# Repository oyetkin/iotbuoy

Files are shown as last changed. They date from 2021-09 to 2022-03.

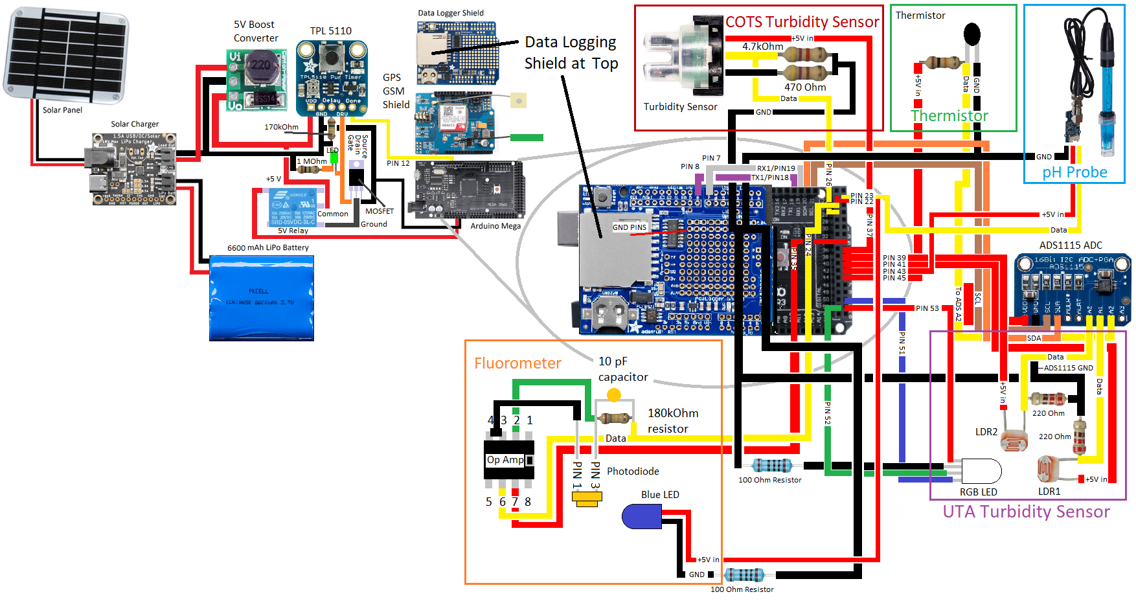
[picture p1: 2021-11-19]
ElectricalSchematic.png

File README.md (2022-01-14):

# IoT Buoy



Lake Erie Algae Bloom 2019, (Image credit NOAA)

An open source, low-cost envirnmental buoy designed to monitor the health of lakes, rivers, estuaries and tidal regions with particular emphasis on algae blooms.
Designed by [Analytical Mechanics Associates](https://www.ama-inc.com/) and the [Virginia Modeling, Analysis & Simulation Center (VMASC)](https://www.odu.edu/vmasc). This project is compatible with the [Open Data Cube](https://www.opendatacube.org/), which is an open-source platform that can ingest data from a variety of sensors and has the goal of making environmental monitoring simple and highly accessible. An overview of the current progress is posted [here](https://github.com/oyetkin/iotbuoy/blob/main/BuoyPresentation1.pdf)

# Building your Buoy - Buoy Specific Hardware Required

### 1. [Arduino MEGA or ELEGOO MEGA](https://www.amazon.com/ELEGOO-ATmega2560-ATMEGA16U2-Arduino-Compliant/dp/B01H4ZDYCE/ref=asc_df_B01H4ZDYCE/?tag=hyprod-20&linkCode=df0&hvadid=309751315916&hvpos=&hvnetw=g&hvrand=11900577637582741809&hvpone=&hvptwo=&hvqmt=&hvdev=c&hvdvcmdl=&hvlocint=&hvlocphy=9008124&hvtargid=pla-493625544636&psc=1&tag=&ref=&adgrpid=67183599252&hvpone=&hvptwo=&hvadid=309751315916&hvpos=&hvnetw=g&hvrand=11900577637582741809&hvqmt=&hvdev=c&hvdvcmdl=&hvlocint=&hvlocphy=9008124&hvtargid=pla-493625544636)

- [Arduino MEGA R3](https://store.arduino.cc/usa/mega-2560-r3)

- [ELEGOO MEGA R3 (cheaper)](https://www.amazon.com/ELEGOO-ATmega2560-ATMEGA16U2-Arduino-Compliant/dp/B01H4ZDYCE/ref=asc_df_B01H4ZDYCE/?tag=hyprod-20&linkCode=df0&hvadid=309751315916&hvpos=&hvnetw=g&hvrand=11900577637582741809&hvpone=&hvptwo=&hvqmt=&hvdev=c&hvdvcmdl=&hvlocint=&hvlocphy=9008124&hvtargid=pla-493625544636&psc=1&tag=&ref=&adgrpid=67183599252&hvpone=&hvptwo=&hvadid=309751315916&hvpos=&hvnetw=g&hvrand=11900577637582741809&hvqmt=&hvdev=c&hvdvcmdl=&hvlocint=&hvlocphy=9008124&hvtargid=pla-493625544636)

### 2. [Adafruit Boost Converter](https://www.amazon.com/Module-Output-Voltage-Converter-Regulator/dp/B08NCM9ZPQ/ref=pd_lpo_2?pd_rd_i=B08NCM9ZPQ&th=1)

### 3. [SIM 808 GPRS/GSM Shield](https://www.robotshop.com/en/sim808-gps-gprsgsm-arduino-shield-mkf.html)

### 4. [Adafruit Solar Charger](https://www.adafruit.com/product/390?gclid=Cj0KCQiAkZKNBhDiARIsAPsk0Wjwwub03ZPgBxlKg1lHWn5nn0opyzVy_Q3VPSugYz3q11KsZ251EOcaAhBzEALw_wcB)

### 5. [Adafruit Data Logging Shield](https://www.adafruit.com/product/1141?gclid=EAIaIQobChMI9OqQ1tr58QIVzXxvBB3GTgbGEAQYASABEgITQvD_BwE)

- Requires [CR1220 Coin Cell Battery](https://www.grainger.com/product/54ZU79?ef_id=CjwKCAjwmeiIBhA6EiwA-uaeFeCfQyJyafe8bUuabPpTv9V-Dkiohqq99VO3asoSj661ExP630XgBhoCccUQAvD_BwE:G:s&s_kwcid=AL!2966!3!496359975085!!!g!484329633033!&gucid=N:N:PS:Paid:GGL:CSM-2293:99F1R6:20501231&gclid=CjwKCAjwmeiIBhA6EiwA-uaeFeCfQyJyafe8bUuabPpTv9V-Dkiohqq99VO3asoSj661ExP630XgBhoCccUQAvD_BwE&gclsrc=aw.ds)

- [Adafruit Data Logging Shield Board and Schematic](https://github.com/adafruit/Data-Logger-shield)

- [Adafruit Data Logging Shield Fritzing Object](https://github.com/adafruit/Fritzing-Library/blob/master/parts/Adafruit%20Datalogger%20Shield%20v1.fzpz)

### 6. [Adafruit ADS1115 Analog to Digital Converter](https://www.adafruit.com/product/1085?gclid=Cj0KCQjw0emHBhC1ARIsAL1QGNfJ3SJ85uZqejbk4At3gi_rBteSZwTxbq5_mKbJvcHG9wJhS_kqJ54aAu4vEALw_wcB)

- [ADS1115 Hardware Drivers](https://github.com/adafruit/Adafruit_ADS1X15)

- [ADS1115 Board and Schematics](https://github.com/adafruit/ADS1X15-Breakout-Board-PCBs)

- [ADS1115 Fritzing Object](https://github.com/adafruit/Fritzing-Library/blob/master/parts/Adafruit%20ADS1115%2016Bit%20I2C%20ADC.fzpz)

- [ADS1115 Data Sheet](https://cdn-shop.adafruit.com/datasheets/ads1115.pdf)

- [ADS1115 Sample Code](https://learn.adafruit.com/adafruit-4-channel-adc-breakouts/arduino-code)

### 7. [Adafruit 6V 3.5W Solar Panel](https://www.adafruit.com/product/500)

- [Solar Panel Technical Drawing](https://github.com/VoltaicEngineering/Solar-Panel-Drawings/blob/master/Voltaic%20Systems%203.5W%206V%20113x210mm%20DRAWING%20CURRENT%202017%207%2020.pdf)

### 10. [6600 mAh 3.7V Lithium Ion Battery](https://www.adafruit.com/product/353)

### 11. [Adafruit TPL5110 Breakout Board](https://www.adafruit.com/product/3435)

### 12. [Adafruit Power Boost 1000 Breakout Board](https://www.adafruit.com/product/2465?gclid=CjwKCAiA24SPBhB0EiwAjBgkhrGJI_mgLnF6EL7C2EgxJwRfddbmznOh6DxHYULQIVquQbLt4znxhRoCKecQAvD_BwE)

### 12. Housing
- Buoy with CAD files provided [here](https://github.com/oyetkin/iotbuoy/tree/main/CAD_Files)

- Waterproof box

- Your own design

# Fluorometer Design

### 1. [1 x 395 nm LED](https://www.mouser.com/ProductDetail/BIVAR/UV5TZ-390-15?qs=sGAEpiMZZMtaWn5d0uiAD8cVjFdgDZGx%2FUxBqCDWrPM%3D)

### 2. [FDS 100 Photodiode](https://www.thorlabs.us/thorproduct.cfm?partnumber=FDS100)

### 3. [550 nm Cut On Long Pass Filter](https://www.newport.com/p/10CGA-550)

### 4. [Jewler's Resin](https://www.amazon.com/16OZ-Epoxy-Resin-Graduated-Instructions/dp/B0839GN3PF/ref=sr_1_5?keywords=clear%2Bepoxy%2Bresin&qid=1638217693&qsid=146-2373950-0512811&s=arts-crafts&sr=1-5&sres=B08233BV5W%2CB08HN2XCDS%2CB0839GN3PF%2CB098918WFB%2CB084PZG6HK%2CB07S1MLQMJ%2CB084Q87Y8M%2CB07YCVVYFK%2CB099XFL1PK%2CB086L1CDMT%2CB07G5HY79C%2CB07JBKDQZJ%2CB07JB5P76Z%2CB089XZJFG5%2CB097JLGFZF%2CB07QF2XYYX%2CB092HX7SQT%2CB08PF576QC%2CB0823LC5H1%2CB08XQ2S1VQ&th=1)

### 5. [Black ABS Filament (will be useful for turbidity sensor as well)](https://www.amazon.com/HATCHBOX-3D-Filament-Dimensional-Accuracy/dp/B00J0H8EWA/ref=sr_1_3?crid=HBAP4Q1YHOWB&keywords=black%2Babs%2Bfilament%2B1.75%2B1kg&qid=1638217775&qsid=146-2373950-0512811&sprefix=black%2Babs%2Bfila%2Carts-crafts%2C167&sr=8-3&sres=B00J0H8EWA%2CB07XF5KM74%2CB07T2QZSLY%2CB01M6Y2QF1%2CB00MV7T25E%2CB07199449V%2CB00WX4UONO%2CB0919Q91MN%2CB015VGJGPW%2CB00F9MNMAY%2CB018F586ES%2CB08N4MMK6V%2CB089NPTH2W%2CB09H7RKL95%2CB07GFXYVLR%2CB08BR7YCY1&srpt=THERMOPLASTIC_FILAMENT&th=1)

# Turbidity Sensor Design

### 1. [2 x Photoresistors](https://www.amazon.com/gp/product/B01N7V536K/ref=ppx_yo_dt_b_search_asin_image?ie=UTF8&psc=1)

### 2. [1 x RGB LED](https://www.amazon.com/gp/product/B077XGF3YR/ref=ppx_yo_dt_b_search_asin_title?ie=UTF8&th=1)

### 3. [Jewler's Resin](https://www.amazon.com/16OZ-Epoxy-Resin-Graduated-Instructions/dp/B0839GN3PF/ref=sr_1_5?keywords=clear%2Bepoxy%2Bresin&qid=1638217693&qsid=146-2373950-0512811&s=arts-crafts&sr=1-5&sres=B08233BV5W%2CB08HN2XCDS%2CB0839GN3PF%2CB098918WFB%2CB084PZG6HK%2CB07S1MLQMJ%2CB084Q87Y8M%2CB07YCVVYFK%2CB099XFL1PK%2CB086L1CDMT%2CB07G5HY79C%2CB07JBKDQZJ%2CB07JB5P76Z%2CB089XZJFG5%2CB097JLGFZF%2CB07QF2XYYX%2CB092HX7SQT%2CB08PF576QC%2CB0823LC5H1%2CB08XQ2S1VQ&th=1)

### 4. [Black ABS Filament (will be useful for fluorometer as well)](https://www.amazon.com/HATCHBOX-3D-Filament-Dimensional-Accuracy/dp/B00J0H8EWA/ref=sr_1_3?crid=HBAP4Q1YHOWB&keywords=black%2Babs%2Bfilament%2B1.75%2B1kg&qid=1638217775&qsid=146-2373950-0512811&sprefix=black%2Babs%2Bfila%2Carts-crafts%2C167&sr=8-3&sres=B00J0H8EWA%2CB07XF5KM74%2CB07T2QZSLY%2CB01M6Y2QF1%2CB00MV7T25E%2CB07199449V%2CB00WX4UONO%2CB0919Q91MN%2CB015VGJGPW%2CB00F9MNMAY%2CB018F586ES%2CB08N4MMK6V%2CB089NPTH2W%2CB09H7RKL95%2CB07GFXYVLR%2CB08BR7YCY1&srpt=THERMOPLASTIC_FILAMENT&th=1)

# Other Items Required

- SD Card
- Jumper wires
- Header pins
- Solder
- Soldering iron
- Wire strippers
- Heat shrink tubing
- Electrical tape
- DP 100 epoxy
- Rope/anchor OR Rope/mooring OR free-floating

# Other Interesting Sensors

- [BME 680 Temperature, Pressure and Humidity Sensor](https://www.adafruit.com/product/3660)

- [DHT-11 Temperature/Humidity Sensor](https://www.adafruit.com/product/386)

- [DHT-22 Temperature/Humidity Sensor](https://www.adafruit.com/product/385)

- [Waterproof Thermistor](https://www.adafruit.com/product/372)

- [pH Sensor - TEKCOPLUS](https://www.amazon.com/Replacement-Electrode-Connector-Controller-Hydroponics/dp/B09681C36B/ref=sr_1_19?dchild=1&keywords=ph+meter+electrode&qid=1629149917&sr=8-19)
OR
- [pH Sensor - Vernier](https://www.vernier.com/product/ph-sensor/)

- [Turbidity Sensor](https://www.digikey.com/en/products/detail/amphenol-advanced-sensors/TSD-10/4767843?utm_adgroup=Sensors%20%26%20Transducers&utm_source=google&utm_medium=cpc&utm_campaign=Dynamic%20Search_EN_RLSA_Buyers&utm_term=&utm_content=Sensors%20%26%20Transducers&gclid=CjwKCAjwmeiIBhA6EiwA-uaeFRJvJ3rLHPiHJND-PSO5aePXsmi2i962wfCCjfp96LtXLJMJ6MAUsBoClz0QAvD_BwE)

- [MPU 6050 Inertial Measurement Unit (for wave height, direction etc.)](https://www.adafruit.com/product/3886)

# Fabrication

- Read the "Complete Guide to Building Your Very Own Algae Monitoring Buoy"

# Viewing Results

- Download jupyter to your computer and run "Visualization_Notebook.ipynb"

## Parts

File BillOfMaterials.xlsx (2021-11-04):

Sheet: Grey ABS Case
COMPONENT | NAME | UNIT PRICE | QUANTITY | TOTAL PRICE | LINK
Solar Panel | Adafruit 1W Solar Panel | $19.95 | 1 | $19.95 | https://www.adafruit.com/product/3809
Microcontroller | ELEGOO Mega | $15.99 | 2 | $31.98 | https://www.amazon.com/ELEGOO-ATmega2560-ATMEGA16U2-Arduino-Compliant/dp/B01H4ZDYCE?hvadid=309751315916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
LoRa Shield | Dragino Shield | $21.00 | 2 | $42.00 | LoRa Long Range Transceiver Shield 915 MHz (North America) - RobotShop (https://www.robotshop.com/en/lora-long-range-transceiver-shield-915-mhz-north-america.html)
Container | 220×170×110mm (8.6"×6.7"×4.3") Gratury Junction Box, Hinged Cover Stainless Steel Latch IP67 Waterproof Plastic Enclosure for Electrical Project Includes Mounting Plate and Wall Bracket | $12.99 | 1 | $12.99 | https://www.amazon.com/Gratury-Stainless-Waterproof-Electrical-290%C3%97190%C3%97140mm/dp/B08281V2RL?ac_md=3-0-VW5kZXIgJDUw-ac_d_pm_pm_pm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
NTC Thermistor | 10k resistor | $0.55 | 2 | $1.10 | https://www.digikey.com/en/products/detail/murata-electronics/NXFT15XH103FA1B025/5797781
Battery | 3.7 V 2.2 Ah battery | $9.95 | 1 | $9.95 | Lithium Ion Cylindrical Battery - 3.7v 2200mAh : ID 1781 : $9.95 : Adafruit Industries, Unique & fun DIY electronics and kits (https://www.adafruit.com/product/1781)
Battery Management System | Solar Lithium Ion/Polymer charger | $9.95 | 1 | $9.95 | https://www.adafruit.com/product/4755
Data logging shield | MicroSD card breakout board+ | $13.95 | 1 | $13.95 | https://www.adafruit.com/product/1141?gclid=EAIaIQobChMI9OqQ1tr58QIVzXxvBB3GTgbGEAQYASABEgITQvD_BwE
IMU | MPU 6050 | $6.95 | 1 | $6.95 | https://www.adafruit.com/product/3886
Boost Converter | Adafruit 5V Boost Converter | $3.56 | 1 | $3.56 | https://www.adafruit.com/product/4654?gclid=EAIaIQobChMI0a7O6eH38QIVCWxvBB0nXAA6EAQYASABEgIBAvD_BwE
GPRS/GSM/GPS Shield | SIM808 | $39.00 | 1 | $39.00 | https://www.robotshop.com/en/sim808-gps-gprsgsm-arduino-shield.html
LTE SIM7600 Breakout |  | $40.00 | 1 | $40.00 | https://it.aliexpress.com/item/4000224044192.html?spm=a2g0o.detail.1000023.5.168266beAIrhDP
ADC | ADS1115 | $14.95 | 1 | $14.95 | https://www.adafruit.com/product/1085
Wide Angle LED |  | $0.21 | 1 | $0.21 | https://lighthouseleds.com/5mm-diffused-flat-top-led-amber-orange-ultra-bright.html
150 ohm resistor |  | $0.73 | 1 | $0.73 | https://www.mouser.com/ProductDetail/TE-Connectivity-Holsworthy/ROX5SSJ150R?qs=sGAEpiMZZMtlubZbdhIBIMLPczR3K4Ue5uevzLwiHc4%3D
Marine Grade Nylon Rope |  | $24.00 | 1 | $24.00 | 3/16" Polyester Rope - White - QualityNylonRope.com (https://www.qualitynylonrope.com/3-16-polyester-rope/)
Hologram Industrial SIM |  | $6.00 | 1 | $6.00 | https://store.hologram.io/store/global-iot-sim-card/51
DP 100 Epoxy |  | $26.16 | 1 | $26.16 | SCOTCH-WELD Series DP100, Epoxy Adhesive, Dual-Cartridge, 1.64 oz, Clear, Not Specified Work Life - 489J86|100 - Grainger (https://www.grainger.com/product/SCOTCH-WELD-Series-DP100-489J86?req=Customer_Also_Viewed&opr=AZIDPRR_RRAD-051820&analytics=recommendation)
CR1220 Coin Battery for RTC |  | $0.72 | 1 | $0.72 | GRAINGER APPROVED 1220, Button Cell Battery, Lithium, 3V DC, Diameter 0.472 in, Depth 0.078 in - 54ZU79|CR1220 - Grainger (https://www.grainger.com/product/54ZU79?gucid=N:N:PS:Paid:MS:CSM-2293:MOO74J:20501231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)
SD Card |  | $12.49 | 1 | $12.49 | https://www.amazon.com/SanDisk-Extreme-32GB-UHS-I-SDSDXXG-032G-GN4IN/dp/B01J5RHBQ4?ac_md=3-2-MzIgR0I%3D-ac_d_mf_rf_rf&cv_ct_cx=sd+card
Zip Ties |  | $4.99 | 1 | $4.99 | Amazon.com: TR Industrial Multi-Purpose UV Resistant Black Cable Ties, 4 inches, 100 Pack : Electronics (https://www.amazon.com/TR-Industrial-TR88301-Multi-Purpose-Cable/dp/B01018DB2E?s=hi)
JST Connectors |  | $7.99 | 1 | $7.99 | Amazon.com: 10pcs Upgraded Tiny Whoop JST-PH 2.0 Male and Female Connector Cable for Battery JJRC H36 H67 Blade Inductrix E010 E013 : Toys & Games (https://www.amazon.com/Upgraded-Connector-Battery-Inductrix-Eachine/dp/B07NWD5NTN?hvadid=80195684681837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)
Heat shrink tubing |  | $6.49 | 1 | $6.49 | https://www.amazon.com/560PCS-Heat-Shrink-Tubing-Eventronic/dp/B072PCQ2LW?hvadid=198097502341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
5.5 mm Barrel Connectors |  | $1.70 | 2 | $3.40 | FIT0043 DFRobot | Battery Products | DigiKey (https://www.digikey.com/en/products/detail/dfrobot/FIT0043/7597082)
Jumper wires |  | $5.99 | 1 | $5.99 | Amazon.com: EDGELEC 120pcs Breadboard Jumper Wires 10cm 15cm 20cm 30cm 40cm 50cm 100cm Wire Length Optional Dupont Cable Assorted Kit Male to Female Male to Male Female to Female Multicolored Ribbon Cables : Electronics (https://www.amazon.com/EDGELEC-Breadboard-Optional-Assorted-Multicolored/dp/B07GD2BWPY)
Solder |  | $8.99 | 1 | $8.99 | YI LIN 60/40 Solder Tin Lead Rosin Core Solder Wire For Electrical Soldering (0.6mm/100g) - - Amazon.com (https://www.amazon.com/YI-LIN-Electrical-Soldering-0-22lbs/dp/B08RHMPJW3?s=industrial)
 |  |  | Sum | $354.49

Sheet: 3D Printed Buoy
COMPONENT | NAME | UNIT PRICE | QUANTITY | TOTAL PRICE | LINK
Solar Panel | Adafruit 1W Solar Panel | $19.95 | 1 | $19.95 | https://www.adafruit.com/product/3809
Microcontroller | ELEGOO Mega | $15.99 | 2 | $31.98 | https://www.amazon.com/ELEGOO-ATmega2560-ATMEGA16U2-Arduino-Compliant/dp/B01H4ZDYCE?hvadid=309751315916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
White ABS Filament |  | $21.99 | 1 | $21.99 | https://www.hatchbox3d.com/collections/abs-1-75mm/products/3d-abs-1kg1-75-wht
Battery | 3.7 V 6.6 Ah battery | $24.50 | 1 | $24.50 | https://www.adafruit.com/product/353
Battery Management System | Solar Lithium Ion/Polymer charger | $9.95 | 1 | $9.95 | https://www.adafruit.com/product/4755
Data logging shield | MicroSD card breakout board+ | $13.95 | 1 | $13.95 | https://www.adafruit.com/product/1141?gclid=EAIaIQobChMI9OqQ1tr58QIVzXxvBB3GTgbGEAQYASABEgITQvD_BwE
Boost Converter | Adafruit 5V Boost Converter | $3.56 | 1 | $3.56 | https://www.adafruit.com/product/4654?gclid=EAIaIQobChMI0a7O6eH38QIVCWxvBB0nXAA6EAQYASABEgIBAvD_BwE
GPRS/GSM/GPS Shield | SIM808 | $39.00 | 1 | $39.00 | https://www.robotshop.com/en/sim808-gps-gprsgsm-arduino-shield.html
ADC | ADS1115 | $14.95 | 1 | $14.95 | https://www.adafruit.com/product/1085
Silicone Sealant |  | $4.25 | 1 | $4.25 | Amazon.com: Henkel Corporation 908570 2.7 oz Tub Clear Silicone Waterproof Sealant, Single Tube, 2 Fl Oz : Industrial & Scientific (https://www.amazon.com/Loctite-Silicone-Waterproof-2-7-Ounce-908570/dp/B0002BBX3U)
Wide Angle LED |  | $0.21 | 1 | $0.21 | https://lighthouseleds.com/5mm-diffused-flat-top-led-amber-orange-ultra-bright.html
150 ohm resistor |  | $0.73 | 1 | $0.73 | https://www.mouser.com/ProductDetail/TE-Connectivity-Holsworthy/ROX5SSJ150R?qs=sGAEpiMZZMtlubZbdhIBIMLPczR3K4Ue5uevzLwiHc4%3D
Marine Grade Nylon Rope |  | $24.00 | 1 | $24.00 | 3/16" Polyester Rope - White - QualityNylonRope.com (https://www.qualitynylonrope.com/3-16-polyester-rope/)
Folding Grapnel Anchor (If no moorings available) |  | $9.99 | 1 | $9.99 | SUNCOR Folding Grapnel Anchors | West Marine (https://www.westmarine.com/buy/suncor--1-1-2-lb-folding-grapnel-anchor--P005_153_003_004?pCode=598813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)
CR1220 Coin Battery for RTC |  | $0.72 | 1 | $0.72 | GRAINGER APPROVED 1220, Button Cell Battery, Lithium, 3V DC, Diameter 0.472 in, Depth 0.078 in - 54ZU79|CR1220 - Grainger (https://www.grainger.com/product/54ZU79?gucid=N:N:PS:Paid:MS:CSM-2293:MOO74J:20501231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)
SD Card |  | $12.49 | 1 | $12.49 | https://www.amazon.com/SanDisk-Extreme-32GB-UHS-I-SDSDXXG-032G-GN4IN/dp/B01J5RHBQ4?ac_md=3-2-MzIgR0I%3D-ac_d_mf_rf_rf&cv_ct_cx=sd+card
Things Mobile SIM Card with $10 euros ($11.56 pre-loaded) |  | $11.56 | 1 | $11.56 | https://www.thingsmobile.com/business/shop
DP 100 Epoxy |  | $26.16 | 1 | $26.16 | SCOTCH-WELD Series DP100, Epoxy Adhesive, Dual-Cartridge, 1.64 oz, Clear, Not Specified Work Life - 489J86|100 - Grainger (https://www.grainger.com/product/SCOTCH-WELD-Series-DP100-489J86?req=Customer_Also_Viewed&opr=AZIDPRR_RRAD-051820&analytics=recommendation)
JST Connectors |  | $7.99 | 1 | $7.99 | Amazon.com: 10pcs Upgraded Tiny Whoop JST-PH 2.0 Male and Female Connector Cable for Battery JJRC H36 H67 Blade Inductrix E010 E013 : Toys & Games (https://www.amazon.com/Upgraded-Connector-Battery-Inductrix-Eachine/dp/B07NWD5NTN?hvadid=80195684681837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)
5.5 mm Barrel Connectors |  | $8.49 | 1 | $8.49 | Amazon.com: VONVOFF DC Power Pigtail Cable,18AWG Male and Female DC Connector Plug,12V 5A Barrel Jack Connector for CCTV Security Camera and Lighting Power Adapter (10 Pairs) : Electronics (https://www.amazon.com/VONVOFF-Pigtail-Connector-Security-Lighting/dp/B086DKWJ2H?pd_)
Heat shrink tubing |  | $6.49 | 1 | $6.49 | https://www.amazon.com/560PCS-Heat-Shrink-Tubing-Eventronic/dp/B072PCQ2LW?hvadid=198097502341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
Jumper wires |  | $5.99 | 1 | $5.99 | Amazon.com: EDGELEC 120pcs Breadboard Jumper Wires 10cm 15cm 20cm 30cm 40cm 50cm 100cm Wire Length Optional Dupont Cable Assorted Kit Male to Female Male to Male Female to Female Multicolored Ribbon Cables : Electronics (https://www.amazon.com/EDGELEC-Breadboard-Optional-Assorted-Multicolored/dp/B07GD2BWPY)
Solder |  | $8.99 | 1 | $8.99 | YI LIN 60/40 Solder Tin Lead Rosin Core Solder Wire For Electrical Soldering (0.6mm/100g) - - Amazon.com (https://www.amazon.com/YI-LIN-Electrical-Soldering-0-22lbs/dp/B08RHMPJW3?s=industrial)
Real Time Clock |  | $5.99 | 1 | $5.99 | https://www.diymore.cc/products/diymore-ds3231-at24c32-iic-precision-real-time-clock-memory-module-for-arduino
Relay |  | $3.35 | 1 | $3.35 | https://www.digikey.com/en/products/detail/nte-electronics | -inc/R73-1D10-5%2F6/11655844?utm_adgroup=General&utm_source=google&utm_medium=cpc&utm_campaign=Shopping_DK%2BSupplier_NTE%20Electronics&utm_term=&utm_content=General&gclid=CjwKCAjwiY6MBhBqEiwARFSCPvk5GTMvMUVIlpouOziBqMiKNzt5CrrNAmKSv3wozyIH78KfpWLppRoCd9YQAvD_BwE
IRL 7833 MOSFET (needed in fluorometer also) |  | $1.91 | 1 | $1.91 | https://www.mouser.com/ProductDetail/Infineon-IR/IRL7833PBF?qs=9%252BKlkBgLFf3m53w7MGFaEw%3D%3D
 |  |  | Total | $319.14

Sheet: Buoy Sensors
COMPONENT | NAME | UNIT PRICE | QUANTITY | TOTAL PRICE | LINK
pH PROBE
pH Meter |  | $29.50 | 1 | $29.50 | https://www.dfrobot.com/product-1025.html
COMMERCIAL TURBIDITY SENSOR
Turbidity Sensor | TSD-10 | $9.04 | 1 | $9.04 | TSD-10 Amphenol Thermometrics | Sensors, Transducers | DigiKey (https://www.digikey.com/en/products/detail/amphenol-advanced-sensors/TSD-10/4767843)
BME 280 PRESSURE, TEMPERATURE, HUMIDITY SENSOR
BME 280 |  | $14.99 | 1 | $14.99 | https://www.amazon.com/HiLetgo-Atmospheric-Pressure-Temperature-Humidity/dp/B01N47LZ4P
CUSTOM TURBIDITY SENSOR
RGB LED | HV-5RGB25 | $1.05 | 2 | $2.10 | https://www.digikey.com/en/products/detail/inolux-corporation/HV-5RGB25/7604615
Photoresistor | Adafruit photoresistor | $0.95 | 2 | $1.90 | https://www.digikey.com/en/products/detail/adafruit-industries-llc/161/7244927
1 x 100 Ohm Resistor
2 x 220 Ohm Resistors
Magnets
Pipe Cleaners
INERTIAL MEASUREMENT UNIT
IMU | MPU 6050 | $6.95 | 1 | $6.95 | https://www.adafruit.com/product/3886
WATER TEMPERATURE SENSOR
Epoxy Waterproof 10k Thermistor |  | $4.00 | 1 | $4.00 | https://www.adafruit.com/product/372
10 kOhm Resistor
FLUOROMETER
Red Filter | Newport 610 nm filter | $48.00 | 1 | $48.00 | 10CGA-550 Longpass Filter (newport.com) (https://www.newport.com/p/10CGA-550) | https://www.1stoplighting.com/lighting/11-224-10327-0-660832/Nora-Lighting_Lens-for-MR16-NM-100R-MR16.htm?nsoid=2639140&CAWELAID=230004010008913043
Operational Amplifier | OP07 | $2.92 | 1 | $2.92 | https://www.mouser.com/ProductDetail/Analog-Devices/OP07CPZ?qs=WIvQP4zGaninz564Y%252B7wyA%3D%3D
Photodiode | FDS100 | $14.94 | 1 | $14.94 | https://www.thorlabs.us/thorproduct.cfm?partnumber=FDS100
Capacitor | 1 nF | $0.71 | 1 | $0.71 | https://www.mouser.com/ProductDetail/Vishay-Cera-Mite/561R10TCCQ10?qs=ohMLqj34oV1qAxjp44jWYQ%3D%3D
Optically Clear Resin |  | $11.99 | 1 | $11.99 | Amazon.com: Clear Epoxy Resin Art Resin Kit 16 Ounce Crystal Jewelry Resin 2 Part Epoxy Resin Kit with Bonus Measuring Cups Sticks Spreader and Gloves : Arts, Crafts & Sewing
Lens |  | $35.00 | 1 | $35.00 | Thorlabs - LA1540-AB N-BK7 Plano-Convex Lens, Ø1/2", f = 15 mm, AR Coating: 400 - 1100 nm (https://www.thorlabs.com/thorproduct.cfm?partnumber=LA1540-AB)
UV LED |  | $1.99 | 2 | $3.98 | UV5TZ-390-15 Bivar | Mouser (https://www.mouser.com/ProductDetail/Bivar/UV5TZ-390-15?qs=cy%252BcHHACsGLfBNaawfbUXg%3D%3D)
IRL7833 MOSFET |  | $1.91 | 1 | $1.91 | https://www.mouser.com/ProductDetail/Infineon-IR/IRL7833PBF?qs=9%252BKlkBgLFf3m53w7MGFaEw%3D%3D
80 x 20 mm Perf Board |  |  |  | $0.00
220 kOhm Resistor |  |  |  | $0.00
6 x 5.6 Mohm Resistors |  |  |  | $0.00
1 x 0.1 Ohm Resistor |  |  |  | $0.00
Electrical Tape |  |  |  | $0.00
Small vial (roughly 1/2 - 3/4 inch diameter should be fine) |  | $4.79 | 1 | $4.79 | https://www.amazon.com/Glass-Vials-Dram-Pack-12/dp/B002JV89OC
Silicone Grease |  | $4.28 | 1 | $4.28 | https://www.amazon.com/gp/product/B000DZFUPC/ref=ppx_yo_dt_b_search_asin_title?ie=UTF8&psc=1
Felt Pieces |  |  |  | $0.00
Set Screws |  |  |  | $0.00
316 Stainless Steel Shaft |  | $5.19 | 1 | $5.19 | https://www.mcmaster.com/1263K133/
O rings |  | $2.32 | 4 | $9.28 | https://www.mcmaster.com/5308T115/
9 g servo (see column G if not available) |  | $6.99 | 1 | $6.99 | Amazon.com: MMOBIEL SG90 9g Micro Servo Motor Kit for RC Drone/Car/Airplane/Helicopter/Vehicles/Robots/Compatible with Arduino Projects and Raspberry Pi Incl. Screws and 3 Servo Arms : Toys & Games (https://www.amazon.com/MMOBIEL-Airplane-Helicopter-Compatible-Raspberry/dp/B097RD8RB7?s=industrial) | Amazon.com: 4Pcs SG90 9g Micro Servos for RC Robot Helicopter Airplane Controls Car Boat : Toys & Games (https://www.amazon.com/Micro-Servos-Helicopter-Airplane-Controls/dp/B07MLR1498?s=industrial)
 |  |  | Total | $218.46

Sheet: Old PCB
COMPONENT NAME | UNIT PRICE | QUANTITY | TOTAL PRICE | SPECS | LINK
Female Headers, I2C | $0.45 | 2 | $0.90 | 1x4, 2.54mm spacing | https://www.digikey.com/en/products/detail/sullins-connector-solutions/PPTC041LFBN-RC/810144
Female Headers, ESP | $0.98 | 2 | $1.96 | 1x15, 2.54mm spacing | https://www.digikey.com/en/products/detail/sullins-connector-solutions/PPTC151LFBN-RC/810153
Female Header, IR Receiver | $0.42 | 1 | $0.42 | 1x3, 2.54mm spacing | https://www.digikey.com/en/products/detail/sullins-connector-solutions/PPTC031LFBN-RC/810143
Transistor, logic inverting and 38KHz modulation | $0.67 | 2 | $1.34 | SOT-23 package | https://www.digikey.com/en/products/detail/diodes-incorporated/ZXTN07045EFFTA/1557734
Resistors, button and other pullup | $0.10 | 3 | $0.30 | 10K Ohm, 0805 package | https://www.digikey.com/en/products/detail/bourns-inc/CR0805-FX-1002ELF/3593209
Resistors, I2C Pullup | $0.10 | 2 | $0.20 | 2.4K Ohm, 0805 package | https://www.digikey.com/en/products/detail/bourns-inc/CR0805-FX-2401ELF/3784778
Resistors, logic inverter | $0.10 | 1 | $0.10 | 100K Ohm, 0805 package | https://www.digikey.com/en/products/detail/te-connectivity-passive-product/CRG0805F100K/2380829
Resistors, IR LED | $0.10 | 2 | $0.20 | 220 Ohm, 0805 package | https://www.digikey.com/en/products/detail/bourns-inc/CR0805-FX-2200ELF/3784749
Resistors, IR Receiver | $0.10 | 1 | $0.10 | 200 Ohm, 0805 package | https://www.digikey.com/en/products/detail/bourns-inc/CR0805-FX-2000ELF/3784732
Resistors, LED driver | $0.37 | 1 | $0.37 | 100 Ohm, 0805 package | https://www.digikey.com/en/products/detail/koa-speer-electronics-inc/RK73G2ATTD1000D/13576043
Polarized Capacitor, IR Receiver | $0.70 | 1 | $0.70 | Tantalum, 1.25 x 1.05mm pads | https://www.digikey.com/en/products/detail/avx-corporation/F981C105MMA/4005059
Momentary Button (Mode, Trigger) | $0.61 | 2 | $1.22 | 1 Pole 1 throw, 6x6mm | https://www.digikey.com/en/products/detail/apem-inc/MJTP1138BTR/1795451
IR LED | $0.81 | 2 | $1.62 | 950nm IR emitter | https://www.digikey.com/en/products/detail/osram-opto-semiconductors-inc/SFH-4545/2205955
TSOP382X Photodiode | $1.12 | 1 | $1.12 | 950 nm, 38kHz | https://www.digikey.com/en/products/detail/vishay-semiconductor-opto-division/TSOP38238/1681362
ESP32 | $8.99 | 2 | $17.98 |  | https://www.amazon.com/dp/B079PVCF2G?psc=1&ref=ppx_yo2_dt_b_product_details
BME 280 Breakout Board | $14.99 | 1 | $14.99 |  | https://www.amazon.com/HiLetgo-Atmospheric-Pressure-Temperature-Humidity/dp/B01N47LZ4P
 |  | Total | $43.52

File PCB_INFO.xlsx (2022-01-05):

SUBSYSTEM | COMPONENT | PURPOSE | QUANTITY | UNIT COST | TOTAL COST | SYMBOL | FOOTPRINT | LINK
Communications | SIM7600A-H | GPS/GPRS/LTE Chip | 1 | 1 | Waiting on response |  |  | https://www.simcom.com/product/SIM7600G_R2.html
Communications | 3.7V LDO | Regulate voltage to SIM7600A 3.4-4.2V Power Supply | 1 | 0.7 | 0.7 |  |  | https://www.mouser.com/ProductDetail/Texas-Instruments/LP5907UVX37-NOPB?qs=SmtJf7EgX8RlmYCt%2FlRL3A%3D%3D
Communications | MicroFL Connector | GPS/GPRS/LTE Connection | 3 | 1.22 | 3.66 |  |  | https://www.digikey.com/en/products/detail/hirose-electric-co-ltd/U-FL-R-SMT-10/513011
Communications | Micro Simcard holder | Hold Sim Card | 1 | 1.75 | 1.75 |  |  | https://www.digikey.com/en/products/detail/wurth-electronics-inc/693043020611/5047621
Power | IRL7833 | Power Switching | 1 | 1.91 | 1.91 |  |  | IRL7833PBF Infineon / IR | Mouser (https://www.mouser.com/ProductDetail/Infineon/IRL7833PBF)
Power | Diode | Power system | 1 | $0.03 | 0.034 |  |  | https://www.digikey.com/en/products/detail/diodes-incorporated/1N4007-T/76454
Power | 100 kOhm Sliding Potentiometer | Set Delay Period | 2 | $1.50 | 3 |  |  | https://www.digikey.com/en/products/detail/bourns-inc./PTA3043-2015DPA104/6153411
Power | TPL 5110 | Timer/Power MOSFET | 1 | 0.706 | 0.706 |  |  | TPL5110DDCT | Buy TI parts | TI.com (https://www.ti.com/store/ti/en/p/product/?p=TPL5110DDCT)
Power | Solar Panel Barrel Connector | Connect to solar panel | 1 | 0.99 | 0.99 |  |  | https://www.digikey.com/en/products/detail/w%C3%BCrth-elektronik/694108301002/5047524
Power | DC DC Converter | Solar charge management | 1 | 13.06 | 13.06 |  |  | https://www.digikey.com/en/products/detail/analog-devices-inc/LTM4624IY-PBF/4291840
Power | (2 A limit) Relay | Turn on and off board | 1 | 3.96 | 3.96 |  |  | https://www.digikey.com/en/products/detail/omron-electronics-inc-emc-div/G3VM-41AY1/5799756
Power | Switch | On/off switch | 1 | 0.76 | 0.76 |  |  | https://www.digikey.com/en/products/detail/e-switch/EG1218/101726?s=N4IgTCBcDaIKYHMAEBGAnABgMwgLoF8g
Power | 1 Mohm Resistor | TPL 5110 drive pin grounding | 1 | 0.42 | 0.42 |  |  | CHV1206AJW-105ELF Bourns | Mouser (https://www.mouser.com/ProductDetail/Bourns/CHV1206AJW-105ELF?qs=QNEnbhJQKvbtExCLSyT8ig%3D%3D)
Power | MAX17205G | Voltage/current monitor | 1 | 4.19 | 4.19 |  |  | https://www.mouser.com/ProductDetail/Maxim-Integrated/MAX17205G+T?qs=sO%2FZ8XQFeM14gpZbIvukxg%3D%3D
Power | 4.7 V Zener Diode | Prevent current from flowing to done pin unless at least 4.8 volts | 1 | 0.46 | 0.46 |  |  | https://www.digikey.com/en/products/detail/diodes-incorporated/PD3Z284C4V7-7/1629588
Power | 2.2 kOhm Resistor | Allow done pin to be connected to GND | 1 | 0.12 | 0.12 |  |  | https://www.digikey.com/en/products/detail/koa-speer-electronics-inc/RK73H1JRTTD2201F/12314793
Turbidity Sensor | 220 Ohm Resistor | Turbidity Sensor | 2 | 0.2 | 0.4 |  |  | https://www.mouser.com/ProductDetail/ROHM-Semiconductor/KTR18EZPF2200?qs=sGAEpiMZZMvjAcTDbo5QThnsiMdPc2N4pYMPSxNsWmg%3D
Turbidity Sensor | 10 p connector | Connect turbidity sensor | 1 | 1.4 | 1.4 |  |  | https://www.mouser.com/ProductDetail/TE-Connectivity/1658621-1?qs=AplfTeSvkkCrmD6FuTzFgg%3D%3D&mgh=1
Turbidity Sensor | 10 p connector | Connect turbidity sensor | 1 | 1.3 | 1.3 |  |  | https://www.mouser.com/ProductDetail/TE-Connectivity/5103309-1?qs=84A%2FDAdkstL1A8M23HoAPw%3D%3D
Turbidity Sensor | 100 Ohm Resistor | So LED doesn't burn out | 1
Comm Turbidity Sensor | 3 pin JST | Connector | 1 | 0.25 | 0.25 |  |  | https://www.digikey.com/en/products/detail/jst-sales-america-inc./B03B-XASK-1(LF)(SN)/1634731
Comm Turbidity Sensor | 4.7kOhm | Resistor | 1 | 0.7 | 0.7 |  |  | https://www.mouser.com/ProductDetail/Bourns/CHP1206AFX-4701ELF
Comm Turbidity Sensor | 470 Ohm | Resistor | 1 | 0.32 | 0.32 |  |  | https://www.mouser.com/ProductDetail/Vishay/RCC1206470RFKEA
Fluorometer | 1 nF Capacitor | Fluorometer Smoothing | 1 | 0.33 | 0.33 |  |  | NFM21CC102R1H3D Murata Electronics | Mouser (https://www.mouser.com/ProductDetail/Murata/NFM21CC102R1H3D)
Fluorometer | 0.1 Ohm Resistor | Sensor Gain | 1 | 0.51 | 0.51 |  |  | https://www.digikey.com/en/products/detail/ohmite/WHBR10FET/678833
Fluorometer | LM358 Op Amp | Transimpedance Amplifier Signal | 1 | 0.9 | 0.9 |  |  | https://www.mouser.com/ProductDetail/Texas-Instruments/TL031IP?qs=odmYgEirbwxA1%252BIWuhLCrQ%3D%3D&mgh=1
Fluorometer | IRL7833 | Power Switching | 1 | 1.91 | 1.91 |  |  | IRL7833PBF Infineon / IR | Mouser (https://www.mouser.com/ProductDetail/Infineon/IRL7833PBF)
Fluorometer | 100 Ohm Resistor | So LED doesn't burn out | 1 | 0.32 | 0.32 |  |  | https://www.mouser.com/ProductDetail/Vishay/RCC1206100RFKEA
Fluorometer | 3 pin JST | Connector | 1 | 0.25 | 0.25 |  |  | https://www.digikey.com/en/products/detail/jst-sales-america-inc./B03B-XASK-1(LF)(SN)/1634731
Fluorometer | 36 Mohm Resistor | Sensor Gain | 1 | 0.72 | 0.72 |  |  | CRCW120636M0JPTAHR Vishay / Dale | Mouser (https://www.mouser.com/ProductDetail/Vishay/CRCW120636M0JPTAHR?qs=sGAEpiMZZMsDgH01pahWBgNLWPHBBwkbPRWtvQgSyR0%3D)
Thermistor | 10k Resistor | Voltage Divider |  |  | 0
Thermistor | 3 pin JST | Connector | 1 | 0.25 | 0.25 |  |  | https://www.digikey.com/en/products/detail/jst-sales-america-inc./B03B-XASK-1(LF)(SN)/1634731
Data Management | SD Card Slot | Micro SD card holder | 1 | 2.12 | 2.12 |  |  | 1040310811 Molex | Connectors, Interconnects | DigiKey (https://www.digikey.com/en/products/detail/molex/1040310811/2370379)
Biofouling | 3 pin JST for stepper motor | Connector | 2 | 0.26 | 0.52 |  |  | https://www.mouser.com/ProductDetail/TE-Connectivity/640457-3?qs=sGAEpiMZZMsyYdr3R27aV9Cjae2oalzY
 |  |  |  |  | 50.86
 | Lock in amplifier |  | 1 |  | 0
 | DHT11 |  | 1 |  | 0
 | ADS1115 | Chip Shortage | 1 |  | 0
 | MPU6050 | Chip Shortage | 1 |  | 0
 | INA260 | Chip Shortage | 1 |  | 0
 | Adjustable Gain? | https://www.digikey.com/en/products/detail/amphenol-piher-sensing-systems/PTC15GV02-106A2020-E/14695237

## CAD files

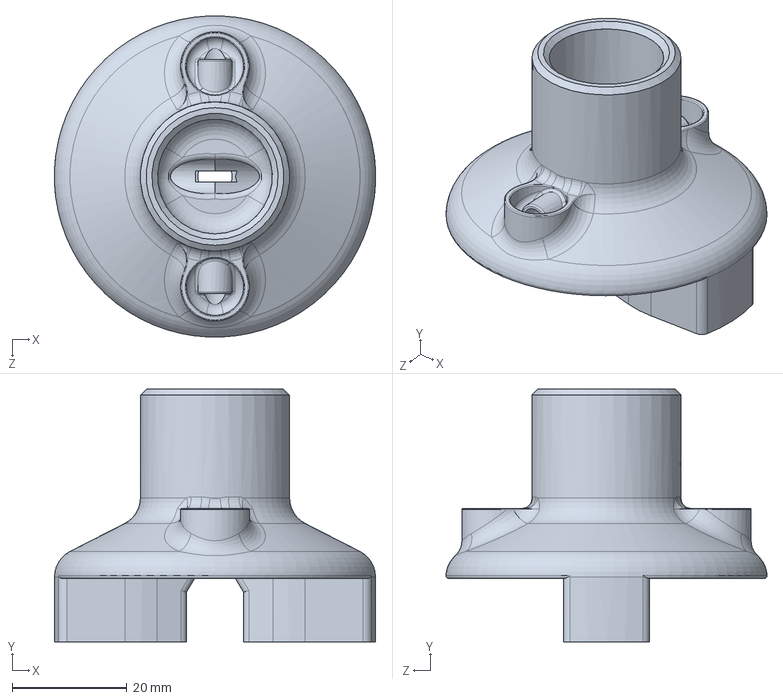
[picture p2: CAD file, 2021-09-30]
CAD_Files/WS 1_Main Body v2.SLDPRT
56.0 x 44.0 x 55.9 mm

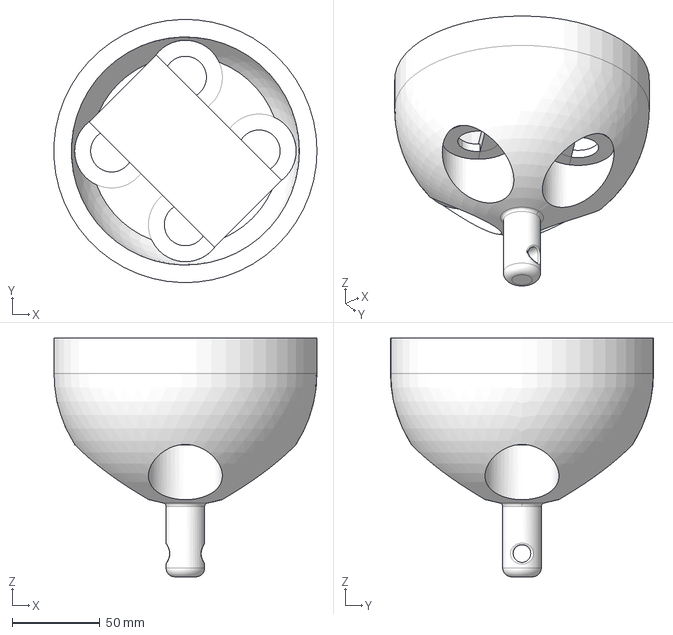
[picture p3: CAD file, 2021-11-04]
CAD_Files/Buoy3DBase.FCStd
149.9 x 149.9 x 136.0 mm

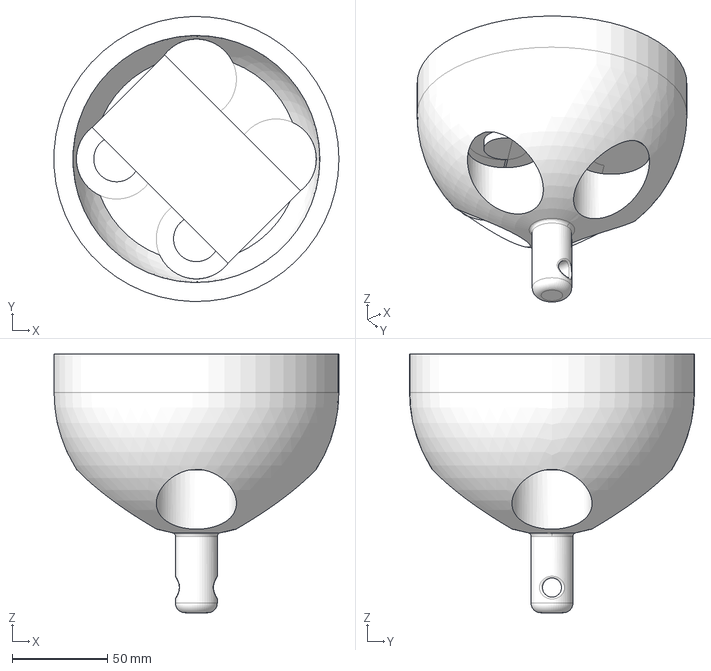
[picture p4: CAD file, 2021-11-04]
CAD_Files/Buoy3DBase-Body.step
149.9 x 149.9 x 136.0 mm

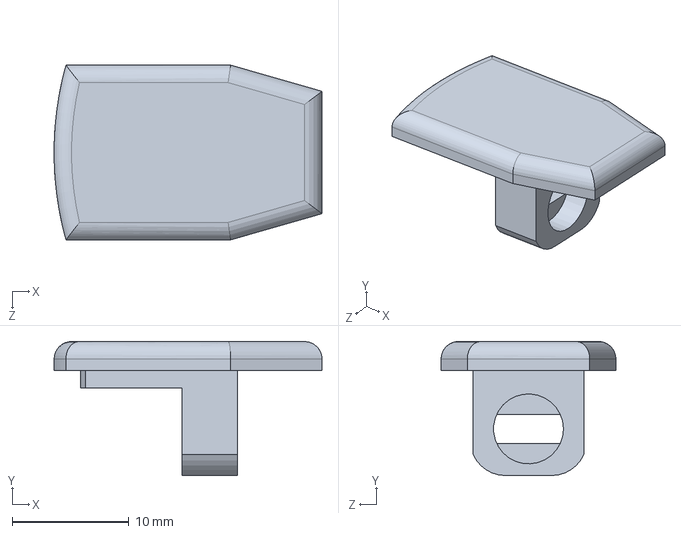
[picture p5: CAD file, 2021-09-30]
CAD_Files/LDR mount v2.SLDPRT
23.0 x 11.5 x 15.0 mm

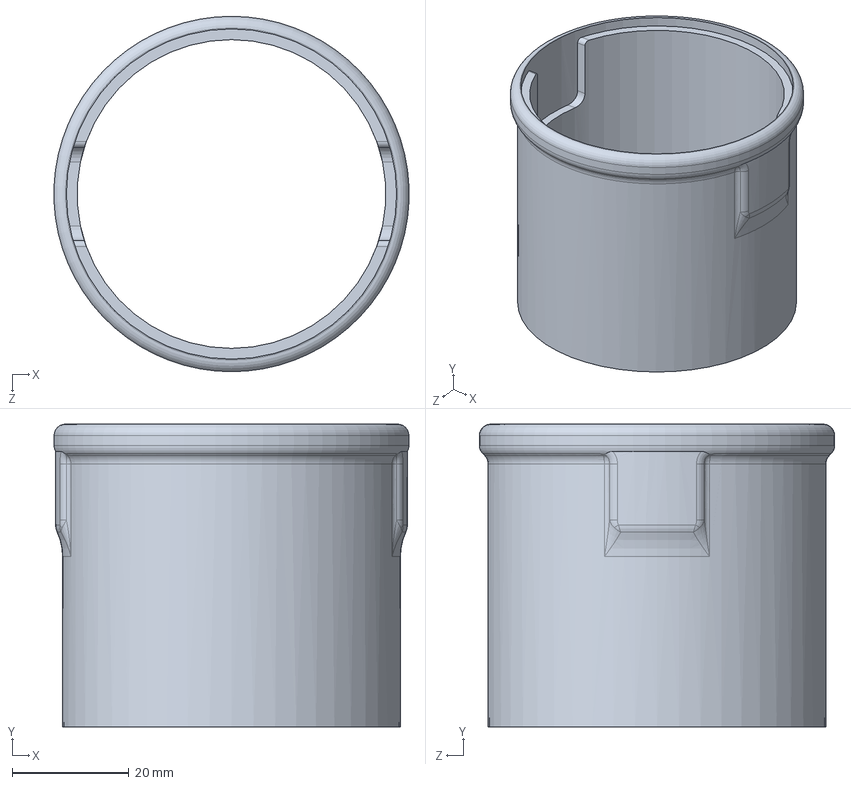
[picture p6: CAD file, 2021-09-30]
CAD_Files/WS 1_Shroud v2.SLDPRT
60.9 x 52.0 x 61.0 mm

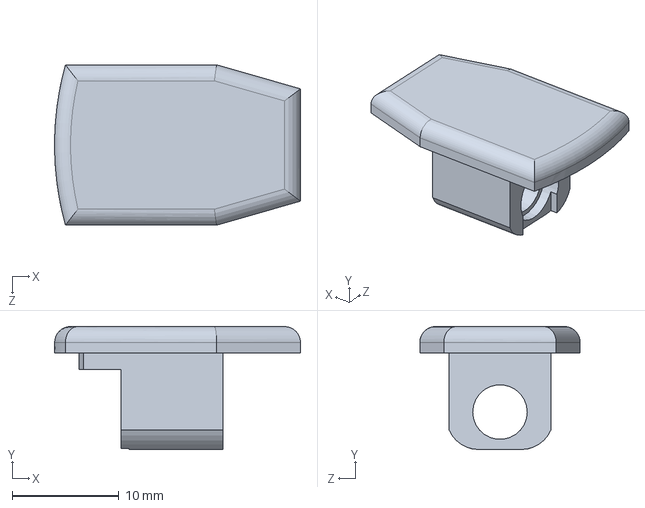
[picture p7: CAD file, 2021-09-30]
CAD_Files/LED mount v2.SLDPRT
23.0 x 11.5 x 15.0 mm

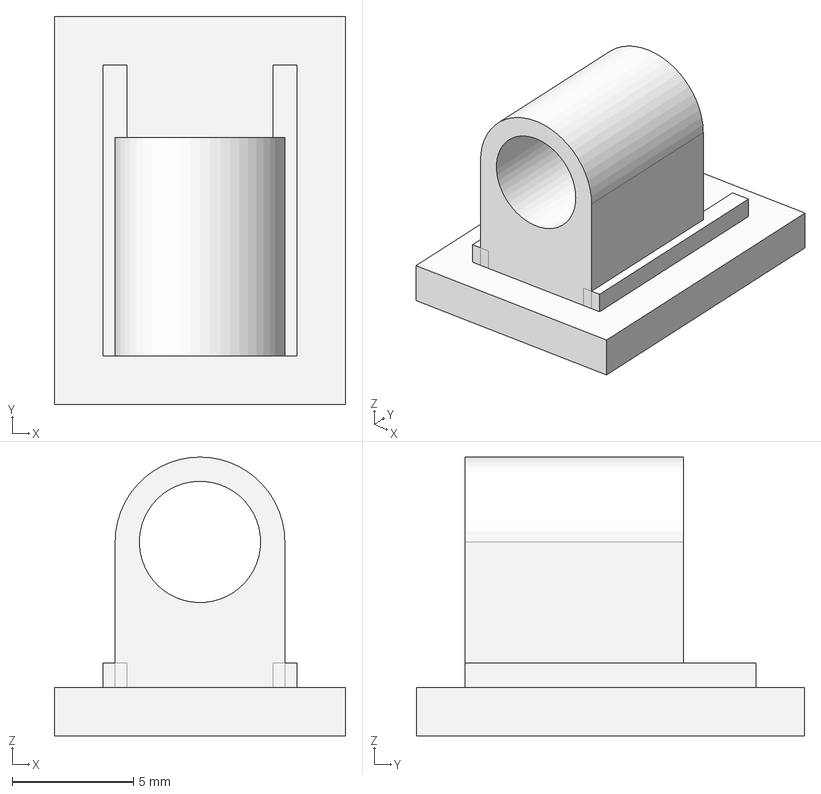
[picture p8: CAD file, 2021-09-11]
CAD_Files/FluorometerLEDHolder.step
12.0 x 16.0 x 11.5 mm

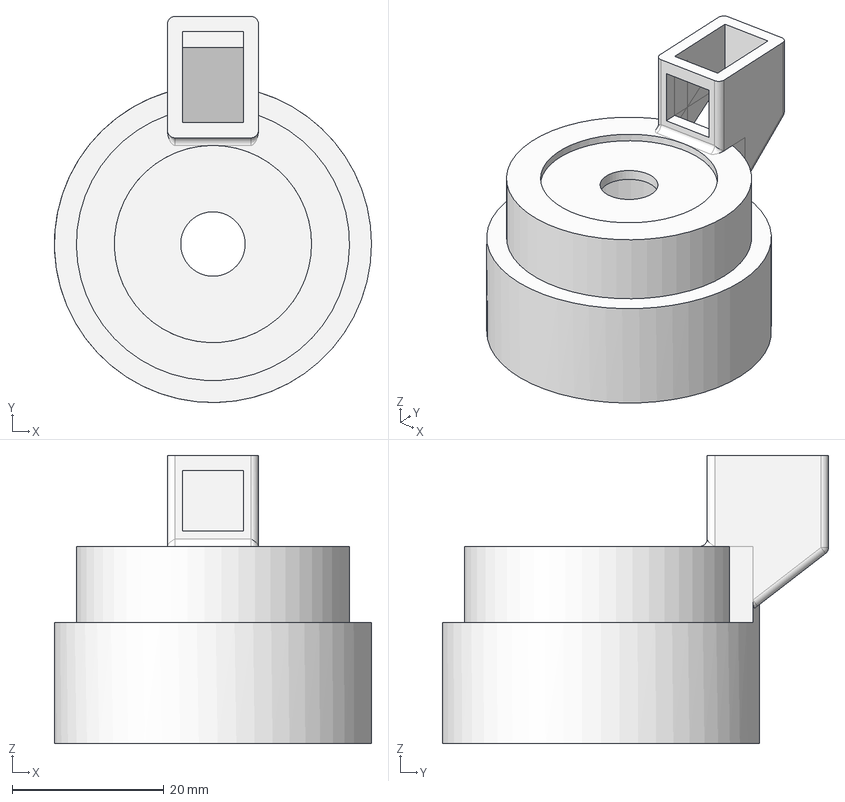
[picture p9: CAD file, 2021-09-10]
CAD_Files/Fluorometer.step
41.8 x 50.9 x 38.0 mm

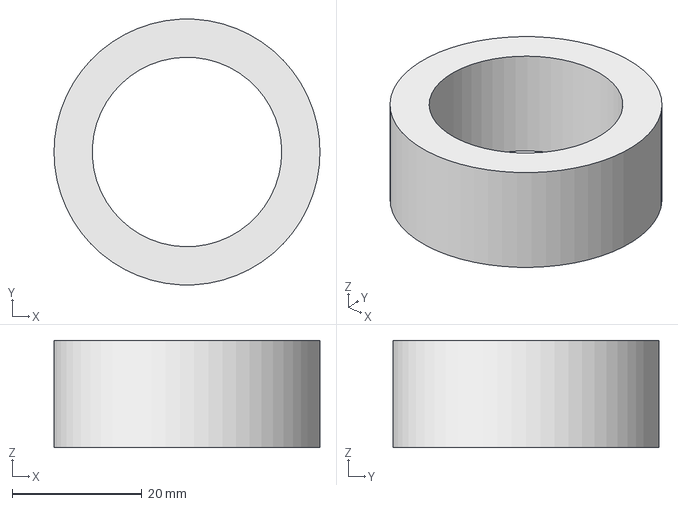
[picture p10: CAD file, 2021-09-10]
CAD_Files/TurbidityAdapter1.FCStd
41.0 x 40.9 x 16.5 mm

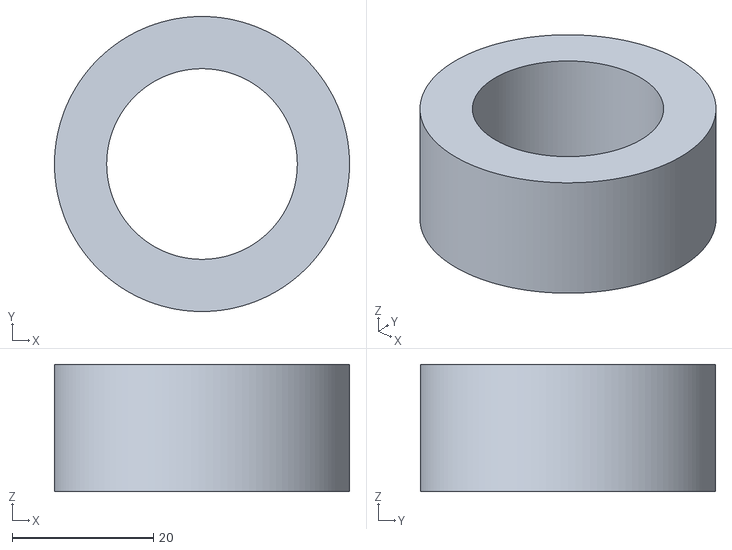
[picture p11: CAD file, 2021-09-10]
CAD_Files/UTASensorAdapter1.stl
41.8 x 41.8 x 18.0

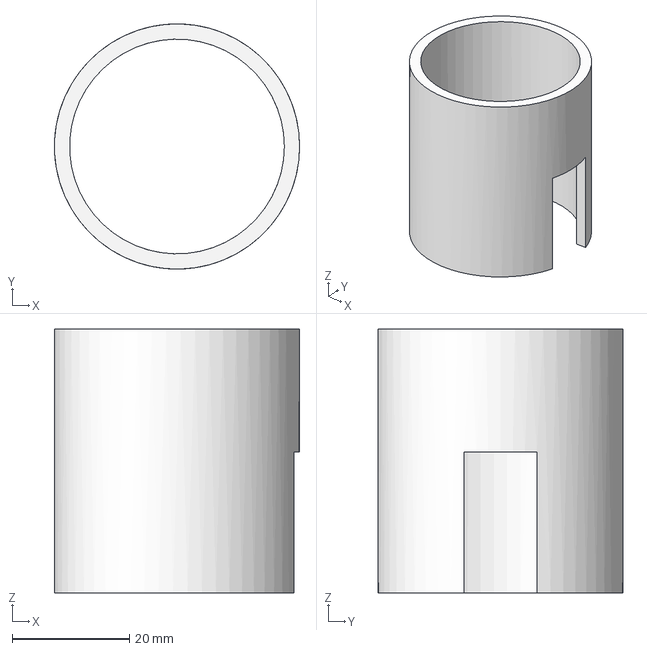
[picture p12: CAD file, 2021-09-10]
CAD_Files/FluorometerShroud.step
41.8 x 41.8 x 45.0 mm

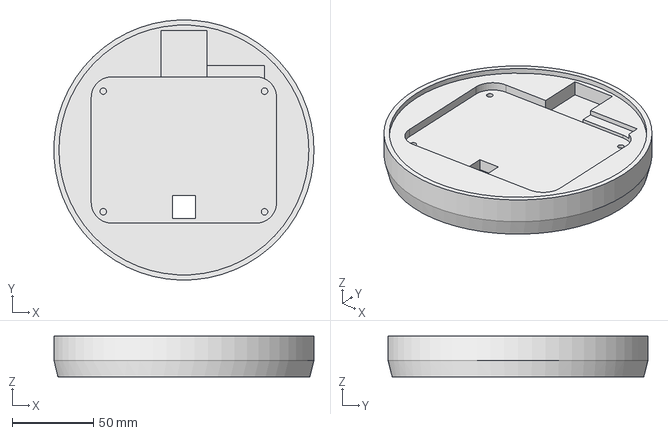
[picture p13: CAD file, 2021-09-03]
CAD_Files/Buoy3DTop.FCStd
159.9 x 159.9 x 25.0 mm

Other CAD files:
CAD_Files/UTASensorAdapter.FCStd
CAD_Files/Buoy3DTop-Body.step
CAD_Files/Buoy3DBase-Body.iges
CAD_Files/Buoy3DBase-Body.stl
CAD_Files/Buoy3DTop-Body.iges
CAD_Files/Buoy3DTop-Body.stl
CAD_Files/Fluorometer.FCStd
CAD_Files/Fluorometer.iges
CAD_Files/Fluorometer.stl
CAD_Files/FluorometerLEDHolder.FCStd
CAD_Files/FluorometerLEDHolder.iges
CAD_Files/FluorometerLEDHolder.stl
CAD_Files/FluorometerShroud.FCStd
CAD_Files/FluorometerShroud.iges
CAD_Files/FluorometerShroud.stl
CAD_Files/LDR mount v2.STL
CAD_Files/LED mount v2.STL
CAD_Files/TurbidityAdapter1.stl
CAD_Files/WS 1_Main Body v2.STL
CAD_Files/WS 1_Shroud v2.STL

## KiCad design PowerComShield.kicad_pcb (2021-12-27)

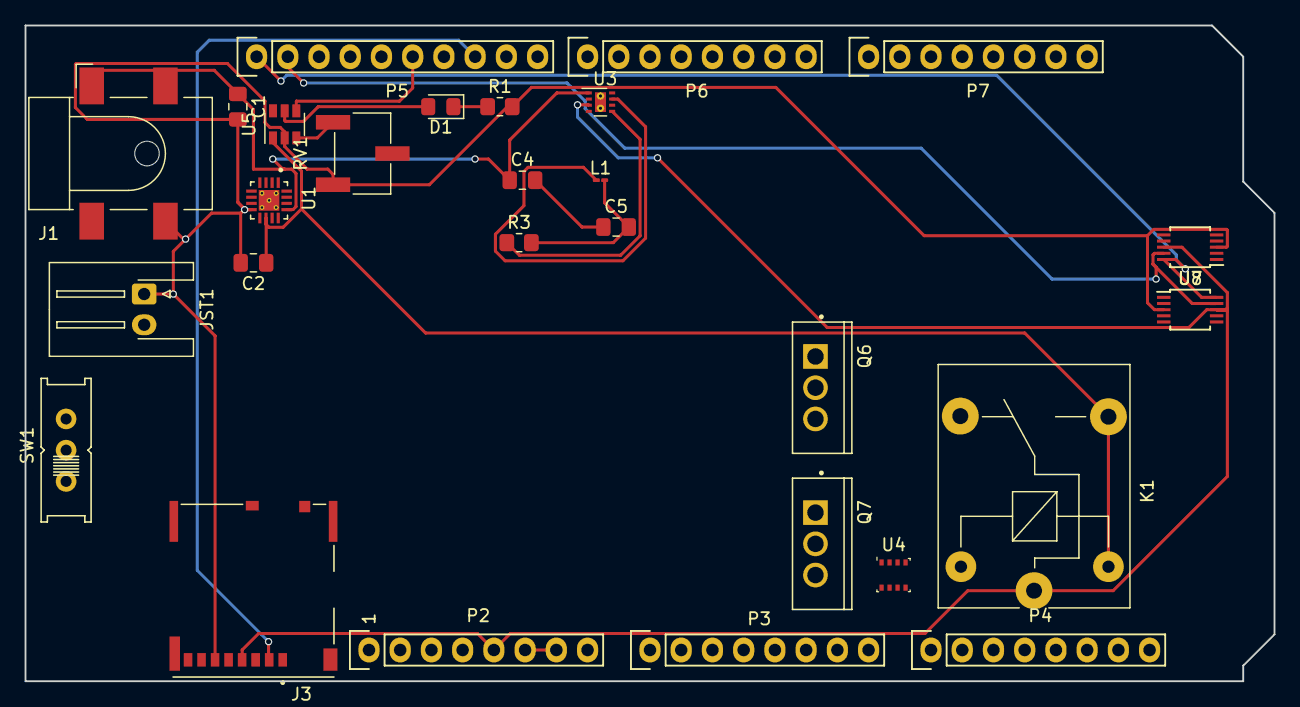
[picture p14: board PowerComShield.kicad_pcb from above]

Board: 4 copper layers, 101.6 x 53.3 mm, 28 parts (0 on the bottom side), 16 nets.

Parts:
C1: 1uF; C_0805_2012Metric_Pad1.18x1.45mm_HandSolder
C2: 4.7 uF; C_0805_2012Metric_Pad1.18x1.45mm_HandSolder
C4, C5: 10 uF; C_0805_2012Metric_Pad1.18x1.45mm_HandSolder
D1: D; D_0805_2012Metric_Pad1.15x1.40mm_HandSolder
J1: Barrel_Jack; BarrelJack_CLIFF_FC681465S_SMT_Horizontal
J3: Micro_SD_Card; MOLEX_503398-1892
JST1: Conn_01x02; JST_XH_S2B-XH-A-1_1x02_P2.50mm_Horizontal
K1: SANYOU_SRD_Form_C; Relay_SPDT_SANYOU_SRD_Series_Form_C
L1: 15 uH; L_01005_0402Metric_Pad0.57x0.30mm_HandSolder
P2: Power; Socket_Strip_Arduino_1x08
P3, P4: Analog; Socket_Strip_Arduino_1x08
P5: PWM; Socket_Strip_Arduino_1x10
P6: PWM; Socket_Strip_Arduino_1x08
P7: Communication; Socket_Strip_Arduino_1x08
Q6, Q7: Q_PMOS_GDS; TO254P1067X483X3124-3P
R1: 1 MOhm; R_0805_2012Metric_Pad1.20x1.40mm_HandSolder
R3: 400 kohm; R_0805_2012Metric_Pad1.20x1.40mm_HandSolder
RV1: R_POT; Potentiometer_Bourns_3269W_Vertical
SW1: SW_DPDT_x2; EG1218
U1: BQ24075; QFN50P300X300X100-17N
U3: TPS62125DSG; WSON-8-1EP_2x2mm_P0.5mm_EP0.9x1.6mm_ThermalVias
U4: BME280; Bosch_LGA-8_2.5x2.5mm_P0.65mm_ClockwisePinNumbering
U5: TPL5110; SOT-23-6
U7, U8: ADS1115IDGS; TSSOP-10_3x3mm_P0.5mm

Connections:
+5V: J3.4, K1.1, P2.5, U3.2, U3.3, U7.8, U8.8
/10(**): J3.2, P5.8
/12(**): P5.6, U5.4
/SCL: P5.1, U7.10, U8.10
/SDA: P5.2, U7.9, U8.9
GND: P2.6, P2.7, P5.4
unnamed: C1.1, C4.1, J1.1, U1.13, U3.1
unnamed: C1.2, C2.2, J1.2, J3.6, JST1.1, R1.2, RV1.3, U1.8, U5.2, U7.3, U8.3
unnamed: C2.1, K1.2, K1.3, U1.10, U5.1
unnamed: C4.2, C5.1
unnamed: C5.2, L1.2, R3.2
unnamed: D1.1, R1.1
unnamed: D1.2, U5.5
unnamed: L1.1, U3.7
unnamed: R3.1, U3.5
unnamed: RV1.1, U5.3

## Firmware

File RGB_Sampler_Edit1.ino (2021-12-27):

//Oguz Yetkin OY 8/4/2021
//self-calibrating sensor for Buoy project.  
//each blank measurement will be subtracted from the immediately read color 

#include <Wire.h>
//#include <Adafruit_ADS1015.h>
#include <Adafruit_ADS1X15.h>
//#include <Adafruit_ADS1015.h>
Adafruit_ADS1115 ads;  /* Use this for the 16-bit version */
//Adafruit_ADS1015 ads;     /* Use thi for the 12-bit version */

int red_led = 5;
int green_led = 6;
int blue_led = 7;

int16_t blank_valuer = 0;
int16_t red_value = 0;
int16_t blank_valueg = 0;
int16_t green_value = 0;
int16_t blank_valueb = 0;
int16_t blue_value =  0;
int16_t blank_value2r = 0;
int16_t red_value2 = 0;
int16_t blank_value2g = 0;
int16_t green_value2 = 0;
int16_t blank_value2b = 0;
int16_t blue_value2 =  0;
int delay_intersample = 400;
int delay_intertest = 500;
int delay_blank = 5;  //keep this short
void setup(void)
{
  Serial.begin(9600);
  pinMode(red_led, OUTPUT);
  pinMode(green_led, OUTPUT);
  pinMode(blue_led, OUTPUT);
  digitalWrite(red_led, LOW);
  digitalWrite(green_led, LOW);
  digitalWrite(blue_led, LOW);
  //Serial.println("Hello!");

  //  Serial.println("Getting single-ended readings from AIN0..3");
  //  Serial.println("ADC Range: +/- 6.144V (1 bit = 3mV/ADS1015, 0.1875mV/ADS1115)");

  // The ADC input range (or gain) can be changed via the following
  // functions, but be careful never to exceed VDD +0.3V max, or to
  // exceed the upper and lower limits if you adjust the input range!
  // Setting these values incorrectly may destroy your ADC!
  //                                                                ADS1015  ADS1115
  //                                                                -------  -------
  // ads.setGain(GAIN_TWOTHIRDS);  // 2/3x gain +/- 6.144V  1 bit = 3mV      0.1875mV (default)
  // ads.setGain(GAIN_ONE);        // 1x gain   +/- 4.096V  1 bit = 2mV      0.125mV
  ads.setGain(GAIN_TWO);        // 2x gain   +/- 2.048V  1 bit = 1mV      0.0625mV
  //ads.setGain(GAIN_FOUR);       // 4x gain   +/- 1.024V  1 bit = 0.5mV    0.03125mV
  //ads.setGain(GAIN_EIGHT);      // 8x gain   +/- 0.512V  1 bit = 0.25mV   0.015625mV
  // ads.setGain(GAIN_SIXTEEN);    // 16x gain  +/- 0.256V  1 bit = 0.125mV  0.0078125mV

  ads.begin();
  Serial.println();
  Serial.println("red_value,green_value,blue_value,red_value2,green_value2,blue_value2");
}

void loop(void)
{
  int16_t adc0, adc1, adc2, adc3;

  blank_valuer = ads.readADC_SingleEnded(0);
  blank_value2r = ads.readADC_SingleEnded(1);
  //blank_value2 = ads.readADC_SingleEnded(1);

  delay(delay_blank);
  digitalWrite(red_led, HIGH);
  delay(1000);
  red_value = ads.readADC_SingleEnded(0);
  red_value2 = ads.readADC_SingleEnded(1);
  digitalWrite(red_led, LOW);
  delay(delay_intersample);

  blank_valueg = ads.readADC_SingleEnded(0);
  blank_value2g = ads.readADC_SingleEnded(1);
  //blank_value2 = ads.readADC_SingleEnded(1);
  delay(delay_blank);
  digitalWrite(green_led, HIGH);
    delay(1000);
  green_value = ads.readADC_SingleEnded(0);
  green_value2 = ads.readADC_SingleEnded(1);
  digitalWrite(green_led, LOW);
  delay(delay_intersample);


  blank_valueb = ads.readADC_SingleEnded(0);
  blank_value2b = ads.readADC_SingleEnded(1);
  //blank_value2 = ads.readADC_SingleEnded(1);
  delay(delay_blank);
  digitalWrite(blue_led, HIGH);
  delay(1000);
  blue_value = ads.readADC_SingleEnded(0);
  blue_value2 = ads.readADC_SingleEnded(1);
  digitalWrite(blue_led, LOW);
  delay(delay_intersample);


  //  int16_t red_v=(red_value-blank_value);
  //  int16_t green_v= (green_value-blank_value);
  //  int16_t blue_v= ( blue_value - blank_value);
//  Serial.print(blank_valuer); Serial.print(", ");
//  Serial.print(red_value); Serial.print(", ");
//  Serial.print(blank_valueg); Serial.print(", ");
//  Serial.print(green_value); Serial.print(", ");
//  Serial.print(blank_valueb); Serial.print(", ");
//  Serial.print(blue_value); Serial.print(", ");
//  Serial.print(blank_value2r); Serial.print(", ");
//  Serial.print(red_value2); Serial.print(", ");
//  Serial.print(blank_value2g); Serial.print(", ");
//  Serial.print(green_value2); Serial.print(", ");
//  Serial.print(blank_value2b); Serial.print(", ");
//  Serial.print(blue_value2);


  //Serial.print(blank_valuer); Serial.print(", ");
  Serial.print(red_value-blank_valuer); Serial.print(", ");
  //Serial.print(blank_valueg); Serial.print(", ");
  Serial.print(green_value-blank_valueg); Serial.print(", ");
  //Serial.print(blank_valueb); Serial.print(", ");
  Serial.print(blue_value-blank_valueb); Serial.print(", ");
  //Serial.print(blank_value2r); Serial.print(", ");
  Serial.print(red_value2-blank_value2r); Serial.print(", ");
  //Serial.print(blank_value2g); Serial.print(", ");
  Serial.print(green_value2-blank_value2g); Serial.print(", ");
  //Serial.print(blank_value2b); Serial.print(", ");
  Serial.print(blue_value2-blank_value2b);

  Serial.println();


  //  adc1 = ads.readADC_SingleEnded(1);
  //  adc2 = ads.readADC_SingleEnded(2);
  //  adc3 = ads.readADC_SingleEnded(3);
  //  Serial.print("AIN0: "); Serial.println(adc0);
  //  Serial.print("AIN1: "); Serial.println(adc1);
  //  Serial.print("AIN2: "); Serial.println(adc2);
  //  Serial.print("AIN3: "); Serial.println(adc3);
  //  Serial.println(" ");
  // Serial.println(adc0);

  delay(1);
}

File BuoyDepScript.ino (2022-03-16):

/*
   Install the following libraries:
   Adafruit BME280
   Adafruit Unified Sensor
   Author: Alex Horvath, Analytical Mechanics Associates
   With code contributed from Arjun Tambe and Oguz Yetkin
*/

#include <Wire.h>
#include <Adafruit_BME280.h>
#include <Adafruit_Sensor.h>
#include <TinyGPS++.h>
#include <avr/wdt.h>

#include <Adafruit_ADS1X15.h>

#define DONEPIN  12 // Set the pin to send the done signal to the TPL5110 watchdog

//Create software serial object to communicate with SIM808. Pin 7 is RX on GPRS/GPS/GSM shield and pin 8 is TX for the robotshop GPS/GPRS/GSM shield here
// https://www.robotshop.com/en/sim808-gps-gprsgsm-arduino-shield-mkf.html?gclid=EAIaIQobChMIl-Hpytn58QIVdGxvBB3DMgZVEAQYDSABEgJUg_D_BwE
// If you are using a different GSM/GPS/GPRS module, use the RX/TX pins given in the board specification.

//Adafruit_BME280 bme; // Create a BME 280 instance
//TinyGPSPlus gps;
String device_name = "Ursula_2"; // Name your station
String dataout;

Adafruit_ADS1115 ads;  /* Use this for the 16-bit version */

adsGain_t gain[6] = {GAIN_TWOTHIRDS, GAIN_ONE, GAIN_TWO, GAIN_FOUR, GAIN_EIGHT, GAIN_SIXTEEN};  // create an array of type adsGain_t, which is a struct in the Adafruit_ADS1015.h library
int g = 1;      // set gain to one to begin with
float adc;
float volt;

const int FluorADS = 2;

const int NumSamples = 5; // How many samples do you want each sensor to take
float samples = 0; // This object collects a sum of each sample data, which is then divided by the number of samples to get the average.

//This struct defines a category of measurement, like "temperature" or "humidity."
struct measurement {
  float min_value; //min recordable by senseor
  float resolution; //sensor resolution
  String unit; //e.g. "Celsius"
  String type; //e.g. "temperature"
  float graph_lower; //lowest value to display on graph
  float graph_upper; //highest value for graph
  String hardware_name; //optionally, hardware used to collect the measurement
};

typedef struct measurement Measurement;

//Create an instance of Measurement for each of the kinds of measurements your sensor will record
//the format is {min_value, increment, units, measurement name, graph_min, graph_max, hardware name}

Measurement fluorescence = {0, 0.01, "Relative %", "fluorescence", 0, 100, "Fluorometer"};

void updateSerial()
{
  delay(20);
  while (Serial.available())
  {
    Serial1.write(Serial.read());//Forward what Serial received to Software Serial Port
  }
  while (Serial1.available())
  {
    Serial.write(Serial1.read());//Forward what Software Serial received to Serial Port
  }
}

void UplinkData(measurement m, float dataval)
{
  Serial.flush(); // Make sure that serial is flushed

  Serial1.flush(); // Make sure software serial is flushed

  delay(2000);

  String json = "{\"key\":\"" + device_name + "\",\"measurement_name\":\"" + m.type + "\",\"unit\":\"" + m.unit + "\",\"value\":" + String(dataval) + ",\"timestamp\":\"11/11/11 11:11:11\",\"lat\":\"30\",\"lon\":\"30\"}";
  //  const char *fulljson = json.c_str(); // Because SoftwareSerial truncates pure strings, save json as a char

  // How many bytes the server should expect , how many seconds/1000 the server should wait for those bytes. Set to 120 bytes for now, trouble calculating sizeof(json)
  // Set to 89 if no date time
  // Set to 120 if date time
  Serial1.println("AT+HTTPDATA=" + String(json.length()) + ",10000");

  delay(2000);

  updateSerial();

  delay(2000);
  updateSerial();
  Serial1.println(json);
  delay(5000);
  updateSerial();
  Serial1.println("AT+HTTPACTION=1"); // 1 for post, 0 for get

  delay(5000);

  updateSerial();

  Serial1.println("AT+HTTPREAD"); // Read response, should be 1, 500, 21 and also will say Internal server error even though data has uploaded

  delay(5000);

  updateSerial();

  delay(1000);

}


float readFluorescence()
{
  while(1) // this function constantly adjusts the gain to an optimum level
  {
    adc = ads.readADC_SingleEnded(2);

    if(adc >= 30000 && g > 0)  // if ADC is getting pegged at maximum value and is not the widest voltage range already, reduce the gain
    {
      g--;
      ads.setGain(gain[g]);
    }
    else if(adc <= 70 && g < 5)
    {
      g++;
      ads.setGain(gain[g]);
    }
    else
      break;
  }
  adc = ads.readADC_SingleEnded(2);   // get avg ADC value from channel 2
  volt = voltage(adc, g);  // convert ADC value to a voltage reading based on the gain
  Serial.println(volt);
  return volt;
}


float voltage(float adc, int gain)
{
  float V;
  switch (gain)
  {
    case 0:  // default 2/3x gain setting for +/- 6.144 V
      V = adc * 0.0001875;
      break;
    case 1:  // 1x gain setting for +/- 4.096 V
      V = adc * 0.000125;
      break;
    case 2:  // 2x gain setting for +/- 2.048 V
      V = adc * 0.0000625;
      break;
    case 3:  // 4x gain setting for +/- 1.024 V
      V = adc * 0.00003125;
      break;
    case 4:  // 8x gain setting for +/- 0.512 V
      V = adc * 0.000015625;
      break;
    case 5:  // 16x gain setting for +/- 0.256 V
      V = adc * 0.0000078125;
      break;

    default:
      V = 0.0;
  }
  return V;
}


int SetGain(int ADS1115Pin) {

  while (1) // this function constantly adjusts the gain to an optimum level
  {
    adc = ads.readADC_SingleEnded(2);   // get avg ADC value
    Serial.println(g);
    if (adc >= 30000 && g > 0) // if ADC is getting pegged at maximum value and is not the widest voltage range already, reduce the gain
    {
      g--;
      ads.setGain(gain[g]);
    }
    else if (adc <= 7000 && g < 5)
    {
      g++;
      ads.setGain(gain[g]);
    }
    else
      return g;
  }
}


void setup()
{
  //
//  digitalWrite(DONEPIN, LOW);
  Serial.begin(57600); //Begin serial communication with Arduino and Arduino IDE (Serial Monitor)

  Serial1.begin(57600); //Begin serial communication with Arduino and SIM808

  delay(100);

  ads.begin();

  Serial1.println("AT"); //Once the handshake test is successful, it will back to OK

  updateSerial(); // Return the response to the serial port for display purposes, and print anything from either serial or SoftwareSerial. May be able to remove in actual deployment pending testing

  Serial1.println("AT+CSQ"); //Signal quality test, value range is 0-31 , 31 is the best

  delay(1000);

  updateSerial();

  Serial1.println("AT+CCID"); //Read SIM information to confirm whether the SIM is plugged in

  delay(1000);

  updateSerial();

  Serial1.println("AT+CREG?"); //Check whether it has registered in the network

  delay(1000);

  updateSerial();

  Serial1.println("AT+CGREG?"); // Check to see if the device is registered again

  delay(1000);

  updateSerial();

  Serial1.println("AT+COPS?"); // Returns the mobile network name i.e. T-mobile

  delay(1000);

  updateSerial();

  Serial1.println("AT+cgatt=1");

  delay(1000);

  updateSerial();

  Serial1.println("AT+CMGF=1"); // Set to SMS text mode

  delay(3000);

  updateSerial();

  Serial1.println("AT+SAPBR=3,1,Contype,GPRS"); // Set connection type to GPRS

  delay(3000);

  updateSerial();

  Serial1.println("AT+SAPBR=3,1,APN,hologram"); // Change "TM" to the APN provided by your carrier

  delay(3000);

  updateSerial();

  Serial1.println("AT+CGACT=1,1"); // Perform GPRS attach, which must occur befpre PDP context can be established

  delay(3000);

  updateSerial();

  Serial1.println("AT+SAPBR=1,1"); // Enable bearer 1

  delay(3000);

  updateSerial();

  Serial1.println("AT+SAPBR=2,1"); // Check whether bearer 1 is open

  delay(3000);

  updateSerial();

  Serial1.println("AT+HTTPINIT"); // Initialize HTTP service

  delay(3000);

  updateSerial();

  Serial1.println("AT+HTTPPARA=CID,1"); // Set bearer profile ID

  delay(3000);

  updateSerial();

  Serial1.println("AT+HTTPPARA=URL,http://52.26.55.255:8080/api/v0p1/sensor"); // Server address

  delay(3000);

  updateSerial();

  Serial1.println("AT+HTTPPARA=\"CONTENT\",\"application/json\"");

  delay(3000);

  updateSerial();

  delay(1000);

  UplinkData(fluorescence, readFluorescence());

  delay(4000);

  pinMode(DONEPIN, OUTPUT);
  
  digitalWrite(DONEPIN, HIGH);
}

void loop(){
  
}

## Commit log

2021-08-24 Add files via upload
    This file allows the user to upload data from a device connected to a personal computer directly to the IoT server. This is useful particularly for streaming data using LoRa or other radio communicat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
2021-08-31 Add files via upload
    Working example for GPRS/RTC. You must bend pins 7/8 and 0/1 (TX/RX) on the arduino GPRS shield if you are using an arduino mega.
2021-10-04 Add files via upload
    Added pH calibration
2021-12-27 Add files via upload
    The initial prototype for power and data management shield for the buoy.
    [PowerComShield.kicad_pcb, PowerComShield.sch]
